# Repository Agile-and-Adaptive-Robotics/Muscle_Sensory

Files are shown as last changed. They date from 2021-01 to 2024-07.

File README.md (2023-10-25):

# Muscle-Sensory
Repository for sharing and storing muscle sensory project related information.
- BallisticShield has solid models for creating ballistic shield to protect experimenters from potential catastrophic BPA failure.
- BPA_End_Caps contains solid models for different types of BPA end caps.
- BPA_Static_Characterization_Test contains files and folders for projects that attempt to characterize the relationship between isometric force, pressure, and contraction. Mostly from Lawrence's incomplete Master's project.
- Leak-Fill_tests contains files from Ben Bolen's mechatronics final project. It is designed to test how quickly a BPA can inflate, and a second test to measure how much pressure a BPA might leak over time.
- Muscle_length_sensory should contain files for real-time muscle length sensory projects. It has files from Jake Chung's Master's project, but doesn't appear to have the files from Connor B.'s Master's project using LiquidWire.
- Muscle_Tension_Sensory contains files for muscle tension sensory projects. Currently it has files from part of Jordan Huddleson's Master's project.
- Pulse testing contains files pertaining to force testing of isometric BPAs using pulsing of BPAs. Current has FrequencyIterationBPATestingCode2 contains an Arduino file that is designed to pulse BPAs in a static jig. It was a project by David P., helped by others (including Cody S.). Will include Mo's testing, too.

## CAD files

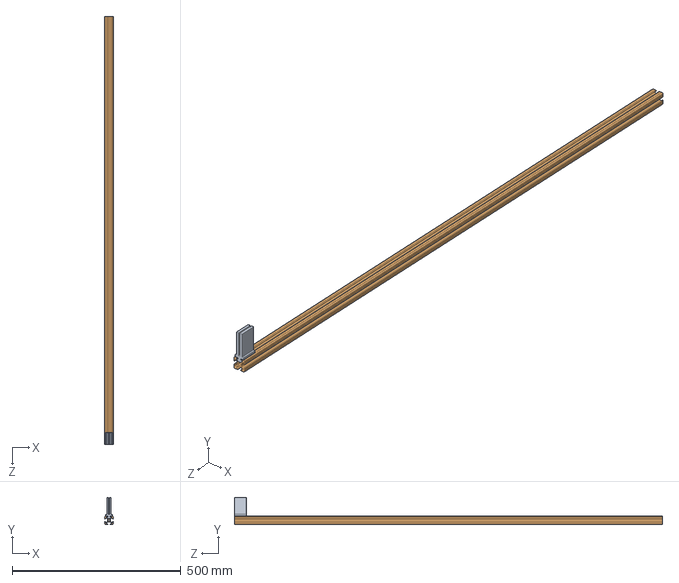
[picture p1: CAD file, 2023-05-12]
BallisticShield/Assem1.SLDASM
25.4 x 80.4 x 1270.0 mm
PolycarbClip
8020-1010 X 50

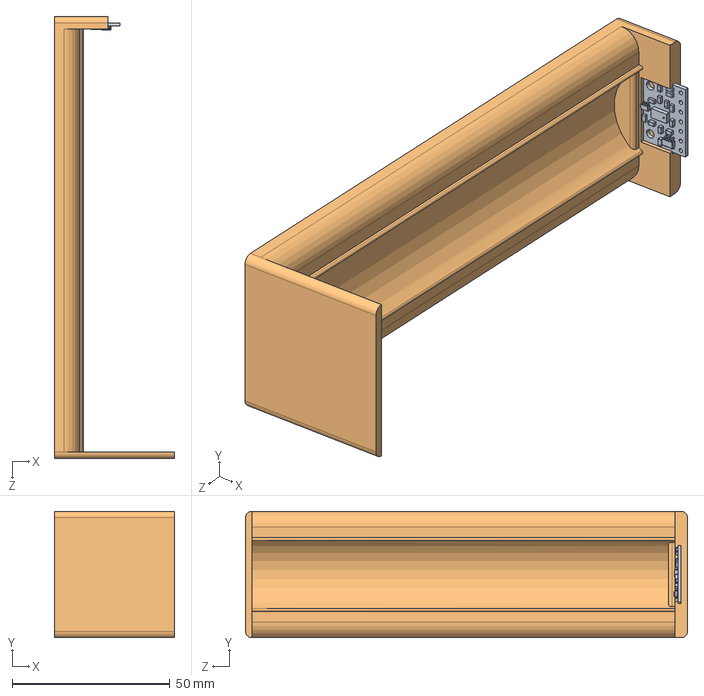
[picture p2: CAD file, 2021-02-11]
Muscle_length_sensory/IR_TOF/circuitTestStand/testStand.SLDASM
38.0 x 40.0 x 140.0 mm
vl53l0x-vl53l1x-vl53l3cx-carrier-model.step
testStand_direct

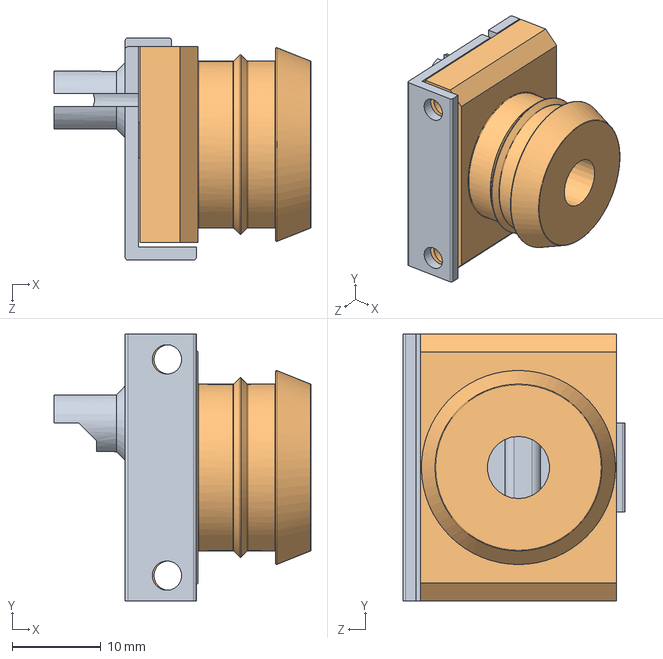
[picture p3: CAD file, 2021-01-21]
Muscle_length_sensory/IR_TOF/sensorEnd.SLDASM
28.9 x 30.0 x 25.0 mm
sensorCap
sensorEnd

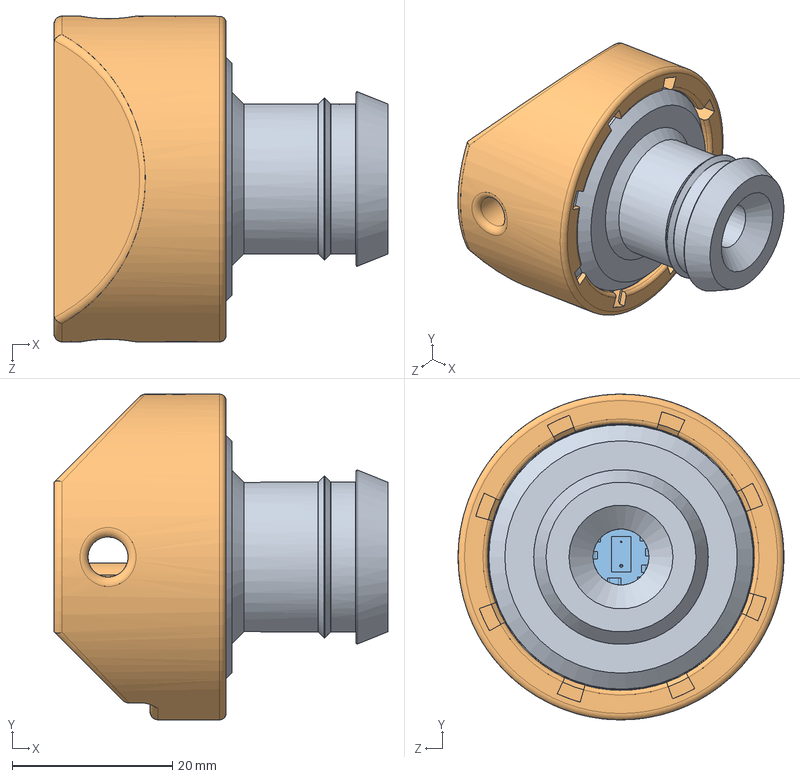
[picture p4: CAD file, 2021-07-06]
Muscle_length_sensory/IR_TOF_circular_housing/circularHousing_withMounting.SLDASM
41.7 x 40.7 x 40.7 mm
sensorEnd_CircularHousing
sensorCap_circularHousingMounting
vl53l0x-vl53l1x-vl53l3cx-carrier-model.step

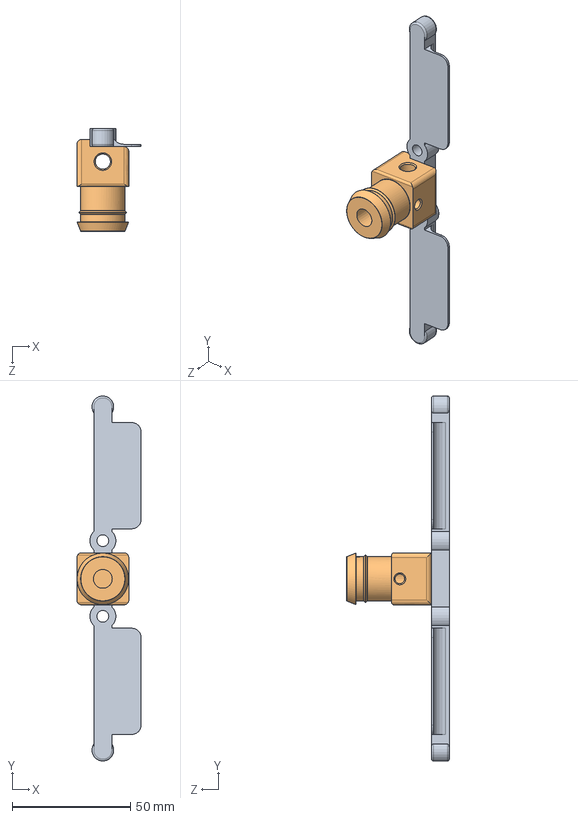
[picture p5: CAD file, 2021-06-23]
Muscle_length_sensory/testFixture/testFixtureAssembly.SLDASM
27.2 x 154.4 x 43.5 mm
80_20_sliding_stabilizer
modified_AARL_Puppy_18_02_01_012_Festo20mm_U10port

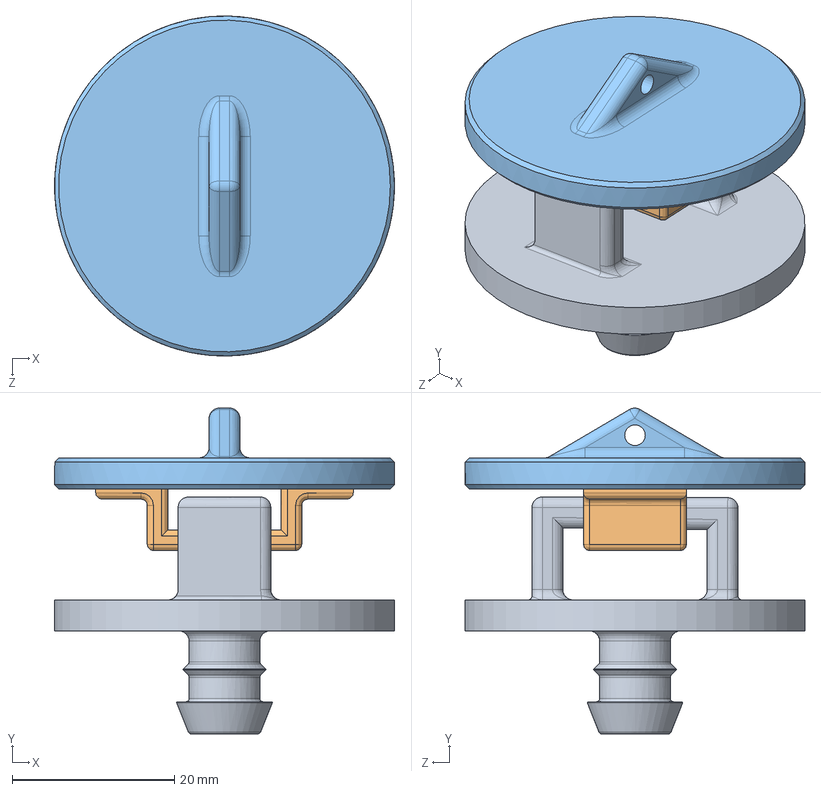
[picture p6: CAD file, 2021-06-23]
Muscle_Tension_Sensory/CAD_Mechanical/AARL_IB-Type_Ib/AARL_IB_002-Compression_Sensor.SLDASM
41.9 x 40.2 x 41.9 mm
AARL_IB_ST_003
AARL_IB_ST_004
AARL_IB_ST_002

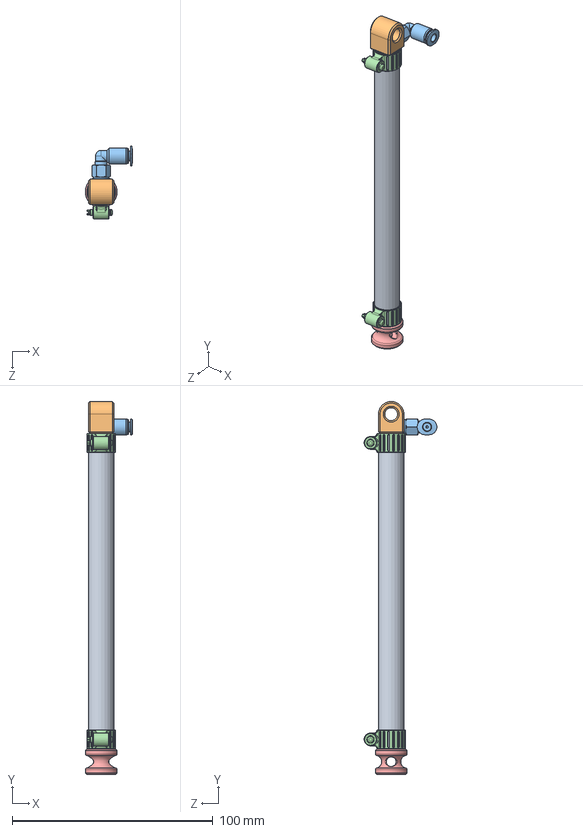
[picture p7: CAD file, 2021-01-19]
BPA_End_Caps/AARL_Puppy_18_02_01_000.SLDASM
23.6 x 185.8 x 36.2 mm
AARL_Puppy_18_02_01_001
AARL_Puppy_18_02_01_002
AARL_Puppy_18_02_01_004-QSML-M3-4
AARL_Puppy_18_02_01_005-SK-8-16 x 2
AARL_Puppy_18_02_01_007

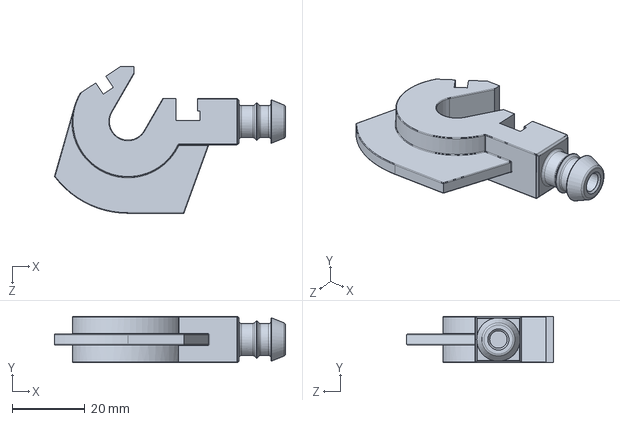
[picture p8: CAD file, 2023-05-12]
BPA_Static_Characterization_Test/Solid_models/BPA10-Hook Assembly.SLDASM
63.3 x 12.7 x 40.2 mm

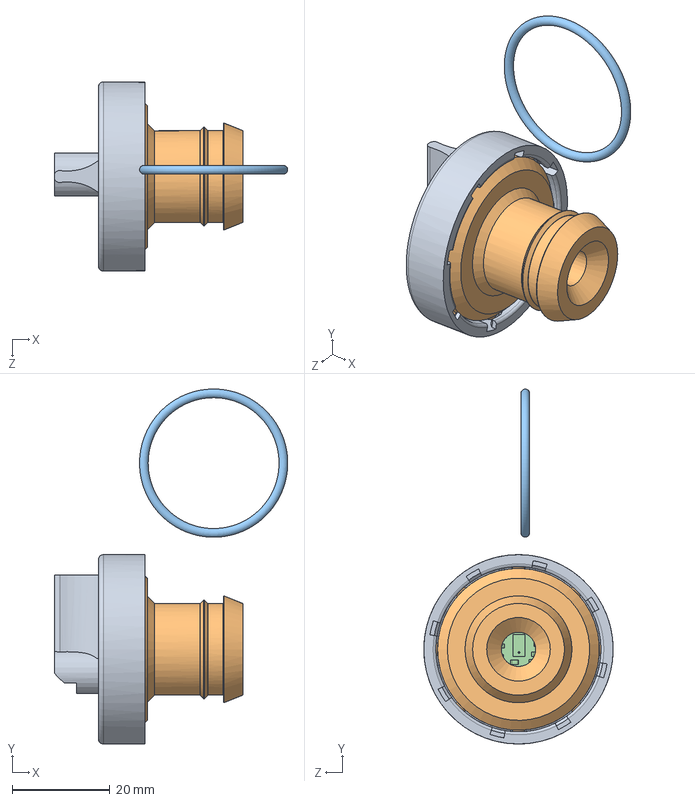
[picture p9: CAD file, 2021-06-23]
Muscle_length_sensory/IR_TOF_circular_housing/circularHousing.SLDASM
47.6 x 72.5 x 38.6 mm
sensorCap_circularHousing
sensorEnd_CircularHousing
vl53l0x-vl53l1x-vl53l3cx-carrier-model (1).step

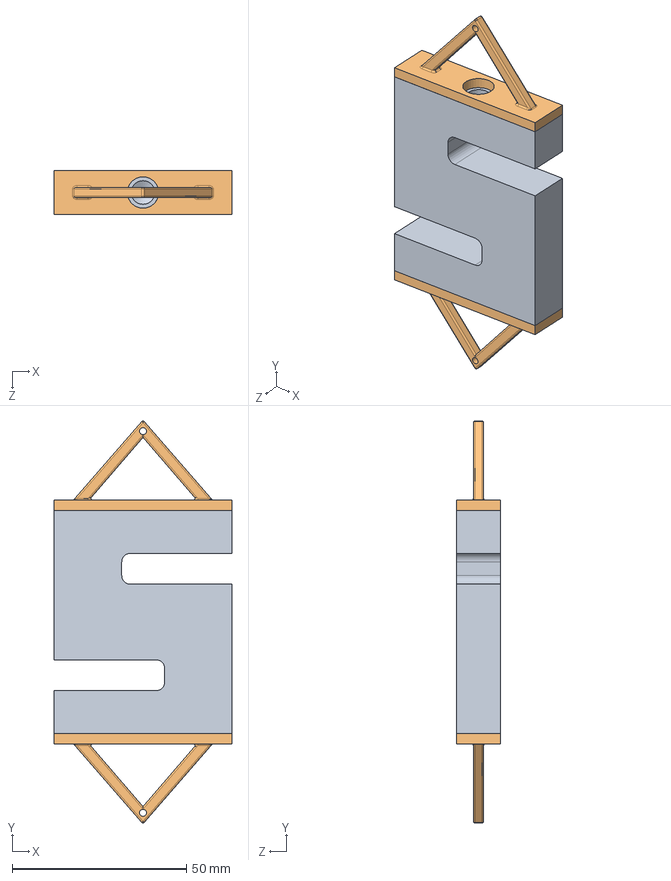
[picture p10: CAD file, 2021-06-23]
Muscle_Tension_Sensory/CAD_Mechanical/AARL_IB-Type_Ib/AARL_IB_001-S_Load_Cell.SLDASM
51.0 x 115.5 x 12.7 mm
AARL_IB_EL_001-S_Load_Cell
AARL_IB_ST_001-S_Plate x 2

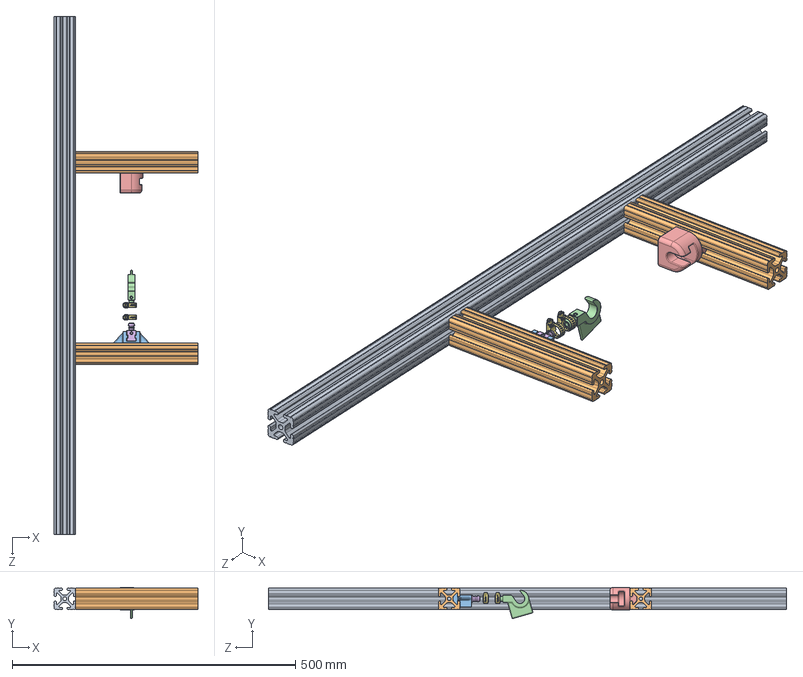
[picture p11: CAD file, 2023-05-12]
BPA_Static_Characterization_Test/Solid_models/Static Test Assembly.SLDASM
254.0 x 54.9 x 914.4 mm
8020-1515 X 36
1515_8_5_CL x 2
BPAConnectionToFrame_10
BPAtoMeter_10
MeterToFrame_002
PlugForFrame_10
AARL_Puppy_18_02_01_009-5388K140_Hose-Clamp x 2

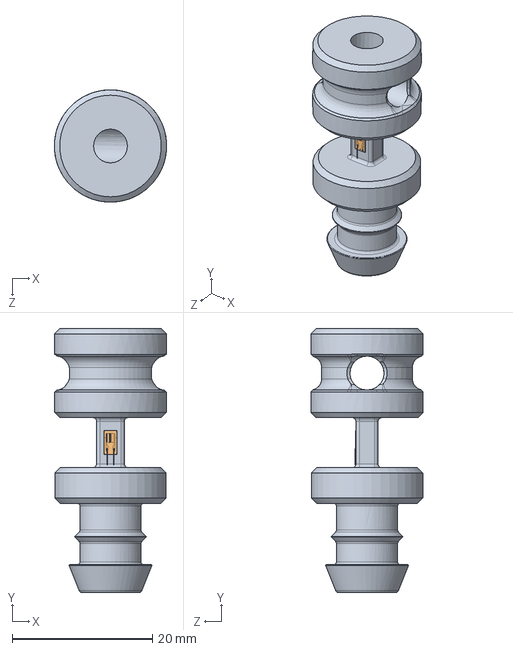
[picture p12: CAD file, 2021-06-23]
Muscle_Tension_Sensory/CAD_Mechanical/AARL_IB-Type_Ib/AARL_IB_003-Strain_Gauge.SLDASM
16.0 x 37.6 x 16.0 mm
AARL_IB_ST_005
AARL_IB_EL_002-Strain_Gauge

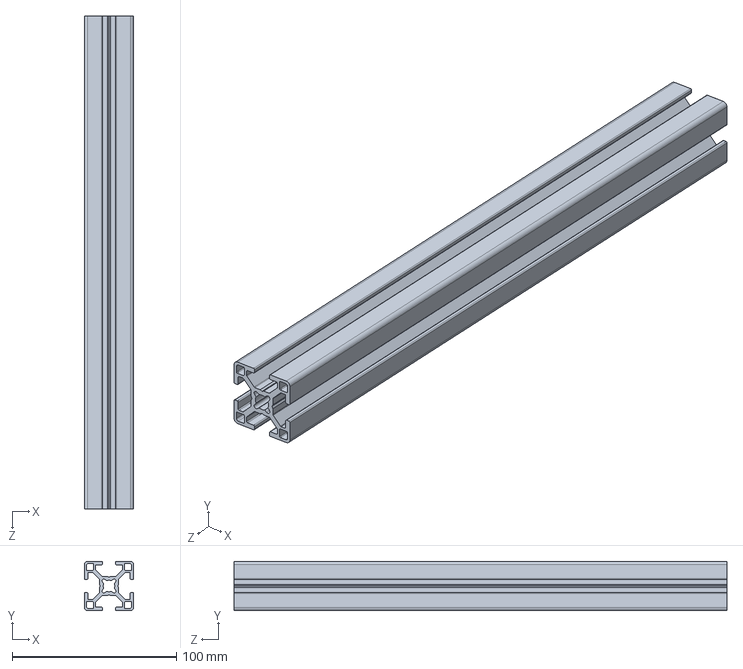
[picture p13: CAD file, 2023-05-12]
BallisticShield/30_Series/30-3030.sldprt
30.0 x 30.0 x 300.0 mm

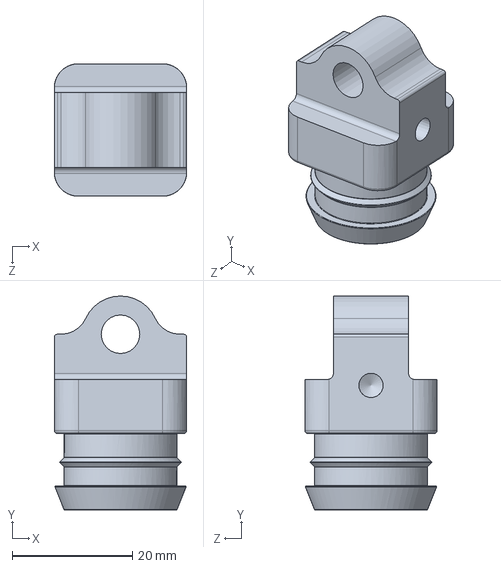
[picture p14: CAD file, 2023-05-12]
BPA_End_Caps/AARL_Puppy_18_02_01_012_Festo20mm_U10port_Law.SLDPRT
22.0 x 35.5 x 22.0 mm

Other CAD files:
BPA_Static_Characterization_Test/Solid_models/Static Test Assembly - 10mm.SLDASM
BPA_Static_Characterization_Test/Solid_models/BPA_Stronger_Mounting_Hooks/fit test.SLDPRT
BPA_Static_Characterization_Test/Solid_models/DesignedParts/Endcap_20mm_Cable.SLDPRT
BPA_Static_Characterization_Test/Solid_models/PlugForFrame_20mm_NoPorts.SLDPRT
BPA_End_Caps/AARL_Puppy_18_02_01_001.SLDPRT
BPA_End_Caps/AARL_Puppy_18_02_01_002.SLDPRT
BPA_End_Caps/AARL_Puppy_18_02_01_002.STL
BPA_End_Caps/AARL_Puppy_18_02_01_003.SLDPRT
BPA_End_Caps/AARL_Puppy_18_02_01_004-QSML-M3-4.sldprt
BPA_End_Caps/AARL_Puppy_18_02_01_005-SK-8-16.SLDPRT
BPA_End_Caps/AARL_Puppy_18_02_01_006.SLDPRT
BPA_End_Caps/AARL_Puppy_18_02_01_007.SLDPRT
BPA_End_Caps/AARL_Puppy_18_02_01_007.STL
BPA_End_Caps/AARL_Puppy_18_02_01_008.SLDPRT
BPA_End_Caps/AARL_Puppy_18_02_01_008.STL
BPA_End_Caps/AARL_Puppy_18_02_01_010.SLDPRT
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

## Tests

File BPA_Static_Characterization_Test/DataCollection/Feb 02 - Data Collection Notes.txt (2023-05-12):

20 mm BPA testing
Already Done: 12 (15) cm, 23 (25.3) cm, 27.5 (30) cm. Need a longer and shorter test.

FEB 02 2022: 

Collect Data for 20mm BPA: 

-----------------------------------------------------------------------------------------------------------
BPA length: 42.7 cm 
 39.7 cm(measured from clamped end to end)

Diameter :20mm

Max contraction length (measured clamp end to end @ 620kPa):  29.6 cm
Contraction: resting length - max contraction length = 39.7 cm - 29.6 cm = 10.1  cm

NOTES:

First attemp to run test, when the BPA was pressurized the bolt connecting the BPA to the load cell pulled out of the threads.
Tried to thread the bolt in further, and was unsuccessful.  Threaded in as far as possible (by hand), and ran test again, appears 
to be holding. Bolt does not appear to be correctly sized, unless the threads on the load cell aren't standard

 -------------------
Kinked: 3.5 cm
-------------------
Kinked: 4.6 cm

NOTE:

Data for last test appears weird. MATLAB command window noted spike, and the pressure spikes off the chart, while the force goes 
off at about 10 o'clock. Saved data, ran the last test again (test 10)

Ran Offset, Test 10, and all data appeared normal. Saved in seperate file, continuing testing.

-------------------
Kinked: 6.9 cm

-----------------------------------------------------------------------------------------------------------
-----------------------------------------------------------------------------------------------------------
BPA length: 12.4 cm 
 9.8 cm(measured from clamped end to end)

Diameter :20mm

Max contraction length (measured clamp end to end @ 620kPa):  7.4 cm
Contraction: resting length - max contraction length = 9.8 cm - 7.4 cm = 2.4 cm

NOTE: 

 -------------------
Kinked: 1.3 cm
-------------------
Kinked: 2.0 cm

-----------------------------------------------------------------------------------------------------------

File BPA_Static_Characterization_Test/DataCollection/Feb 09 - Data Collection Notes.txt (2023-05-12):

Data for Ben

42.7 cm

20 mm BPA testing

FEB 09 2022: 

Collect Data for 20mm BPA: 

-----------------------------------------------------------------------------------------------------------
BPA length: 45.1 cm 
 42.7 cm(measured from clamped end to end)

Diameter :20mm

Max contraction length (measured clamp end to end @ 620kPa):  34.4 cm
Contraction: resting length - max contraction length = 42.7 cm - 34.4 cm = 8.3 cm

NOTES:

20 mm BPA currently installed on knee was measured at 42.7 cm from clamp to clamp, and then a new BPA was cut 
and installed on the test rig.

-------------------
Kinked: 1.0 cm
-------------------
Kinked:  3.0 cm
-------------------
Kinked:  4.0 cm

-----------------------------------------------------------------------------------------------------------
-----------------------------------------------------------------------------------------------------------
BPA length: cm 
 cm(measured from clamped end to end)

Diameter :20mm

Max contraction length (measured clamp end to end @ 620kPa):  cm
Contraction: resting length - max contraction length = cm - cm = cm

NOTE: 

 -------------------
Kinked: cm
-------------------
Kinked:  cm

-----------------------------------------------------------------------------------------------------------

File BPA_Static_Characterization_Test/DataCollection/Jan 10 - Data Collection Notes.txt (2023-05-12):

Jan 10

Comment: Pressure and Load data (check column)

BPA length: 29.8cm 

28.1cm(measured from clamped end to end)

Diameter :10mm
Max contraction length (measured clamp end to end @ 620kPa): 23.6cm
Contraction: resting length - max contraction length = 28.1 - 23.6 = 4.5

-------------------
Kinked:1.7cm
-------------------
Kinked:2.8cm
-------------------
Kinked:4.1cm

#####################################################################################################

BPA length: 27.6 cm 
25.7 cm(measured from clamped end to end)

Diameter :10mm

Max contraction length (measured clamp end to end @ 620kPa): 22.1 cm
Contraction: resting length - max contraction length = 25.7 cm - 22.1 cm = 3.6 cm

 -------------------
Kinked: 0.7 cm
-------------------
Kinked: 1.5 cm
-------------------
Kinked: 3.1 cm

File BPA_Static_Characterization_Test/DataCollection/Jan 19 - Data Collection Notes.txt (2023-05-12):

James's 20mm BPA Adventures

Jan 19 2022: 

Collect Data for 20mm BPA: 

-----------------------------------------------------------------------------------------------------------
BPA length: 25.3 cm 
22.8 cm(measured from clamped end to end)

Diameter :20mm

Max contraction length (measured clamp end to end @ 620kPa):  17.3 cm
Contraction: resting length - max contraction length =  22.8 cm - 17.3 cm = 5.5 cm

NOTE: Data Saved as 23 cm due to not having original (unclamped) length available at start.

 -------------------
Kinked: 0.9 cm
-------------------
Kinked: 1.9 cm

Data Jumped (load cell bolt sliped some) on second to last data set, will repeat the data set to be sure all data is good
-------------------
Kinked: 1.9 cm

Repeated data point

-----------------------------------------------------------------------------------------------------------

BPA length: 15.0 cm 
 12.0 cm(measured from clamped end to end)

Diameter :20mm

Max contraction length (measured clamp end to end @ 620kPa):  9.5 cm
Contraction: resting length - max contraction length =  12.0 cm - 9.5 cm = 2.5 cm

Note: Data Saved as 12 cm due to not having unclamped length available at start. Attemped to resolve the load cell bolt slipage problem by 
inserting a block of nuts and duct tape and using a hose clamp to hold it in place.

 -------------------
Kinked: 1 cm
-------------------
Kinked: 2.0 cm

-------------------
Kinked:  cm

-----------------------------------------------------------------------------------------------------------

BPA length: 30.0 cm 
 27.5 cm(measured from clamped end to end)

Diameter :20mm

Max contraction length (measured clamp end to end @ 620kPa):  20.7 cm
Contraction: resting length - max contraction length = 27.5 cm - 20.7 cm = 6.8 cm

 -------------------
Kinked: 1.4 cm
-------------------
Kinked: 2.3 cm
-------------------
Kinked: 3.4 cm

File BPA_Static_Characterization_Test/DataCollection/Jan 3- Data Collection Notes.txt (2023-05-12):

Jan 3 - Data Collection Notes
---------------------------------
BPA length: 23cm 
21.9cm(measured from clamped end to end)
Diameter :10mm
Max contraction length (measured clamp end to end @ 620kPa): 18.6cm
Contraction: resting length - max contraction length = 21.9 - 18.6 = 3.3

Data Collection set 1: Unkinked
Note: Force is collected using raw arduino output

---------------------------
Kinked:14mm
---------------------------
Kinked: 30mm
comments: Might be too much slack. hence not enough force. 

---------------------------

#######################################################################################################

BPA length: 30cm
28.1cm(measured from clamped end to end)
Diameter :10mm
Max contraction length (620kPa): 24cm
Contraction: resting length - max contraction length = 28.1 -24 = 4.1

Kinked: 1.2cm
----------------------------------
Kinked: 2.2cm
----------------------------------
Kinked: 3.3cm

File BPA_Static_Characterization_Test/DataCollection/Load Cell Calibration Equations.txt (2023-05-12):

10mm 
force (N) = ((Arduino Output*0.1535)-1.963)*4.45

20mm 
force(N) = (Arduino Output*0.392)-4.1786)*4.45

40mm
force(N) = ((ArduinoOutput)*1.395 - 14.661)*4.45

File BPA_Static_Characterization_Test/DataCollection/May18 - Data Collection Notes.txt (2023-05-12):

40mm Data collection:

1) Debugging and checking sensor signals
Data is collected using ValvePWM_mod : no force equation is applied. Reading analogRead for both pressure and force. 
Note: Pressure spikes a lot because of pressure sensor placement

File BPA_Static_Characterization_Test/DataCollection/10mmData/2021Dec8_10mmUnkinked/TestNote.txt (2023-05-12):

BPA length at clamp end: 12cm
Max contraction length:10cm
contraction: 2cm
Pressure Sensor Placement: Outlet of BPA

-------------------------------------------------------------------------------------------------------------------
Inlet Valve Timing: 10ms per 500ms
Outlet Valve Timing: 30ms per 500ms (Note: sub 30ms the valve wouldn't release gas even though it switches) 
	Test 1 and 2 Comments:Pressure settles at about 200kPa when using 30ms for outlet valve :( 

-------------------------------------------------------------------------------------------------------------------
Inlet Valve Timing: 10ms per 500ms
Outlet Valve Timing: 40ms per 500ms

Test 3 : Pressure settles at about 100kPa. 
Test 4: Added tape to cover silencer holes2? Still same shit. 

-------------------------------------------------------------------------------------------------------------------

Inlet Valve Timing: 10ms per 500ms
Outlet Valve Timing: 60ms per 500ms

Test5: 100kPa

Test6: 100kPa 

----------------------------------------------
Inlet Valve Timing: 5ms per 500ms
Outlet Valve Timing: 40ms per 500ms

Test7: 100kpa. 

Test 8: 100kpa.

---------------------------------------------
Inlet Valve Timing: 5ms per 500ms
Outlet Valve Timing: 50ms per 500ms

Test 9: sub 100kpa. 
Test 10:sub 100kpa

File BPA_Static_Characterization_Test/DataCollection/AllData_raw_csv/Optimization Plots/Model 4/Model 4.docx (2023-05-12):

Testing 10mm 13cm vs 20mm40cm parameters:

Model 4: Force = (a0 + a1(e/emax))*pressure + a2(e/emax) + a3;

Force = a3 + a2*(relative strain) + (ao + a1*relativestrain)*Pressure

Regression analysis:

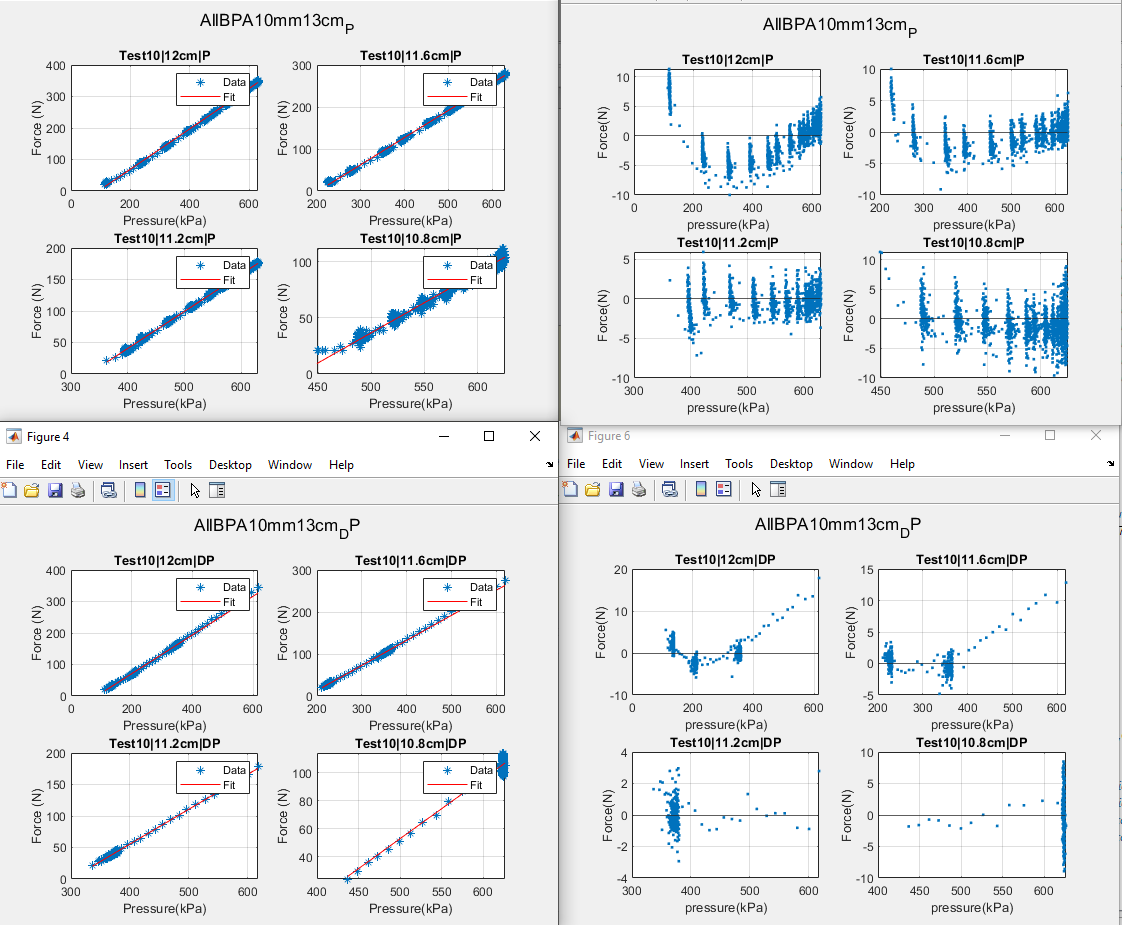
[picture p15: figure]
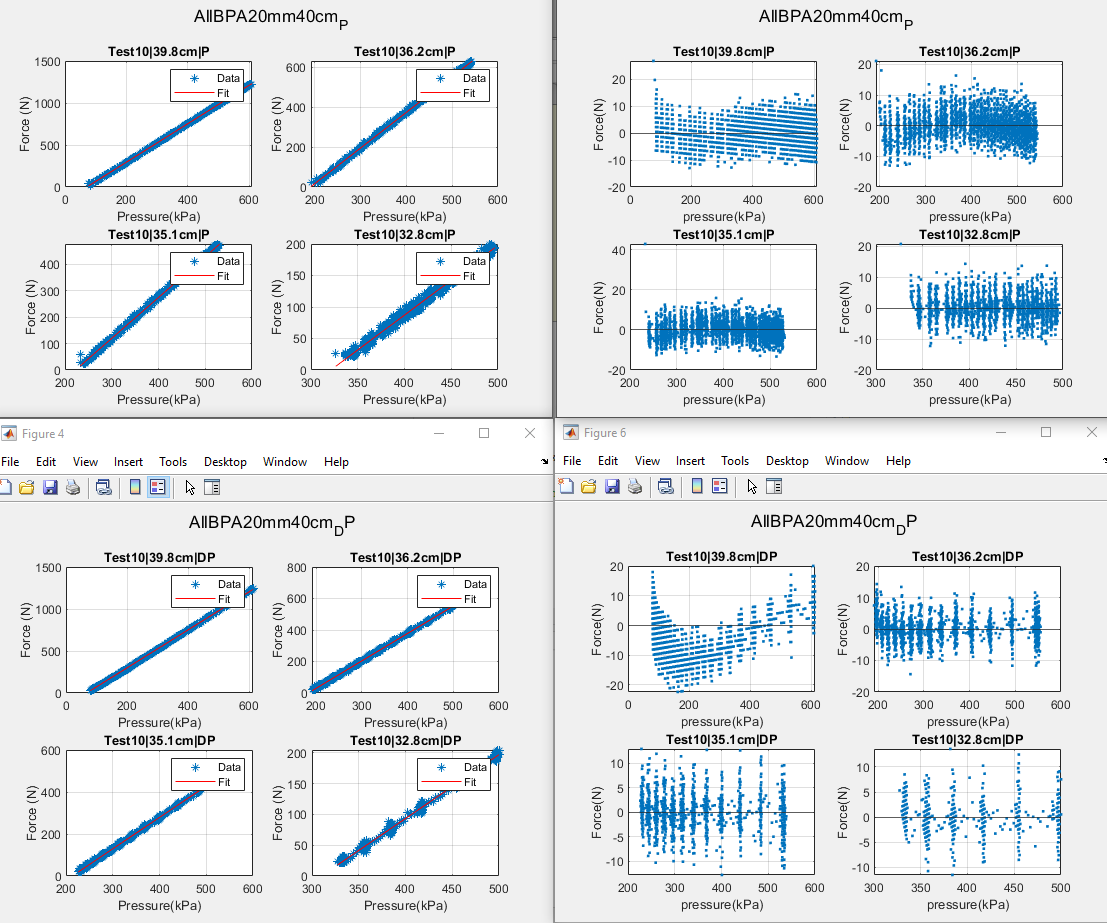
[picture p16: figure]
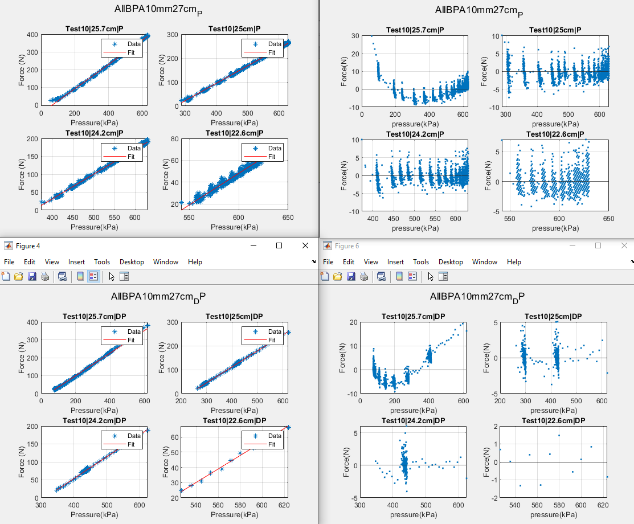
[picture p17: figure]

\

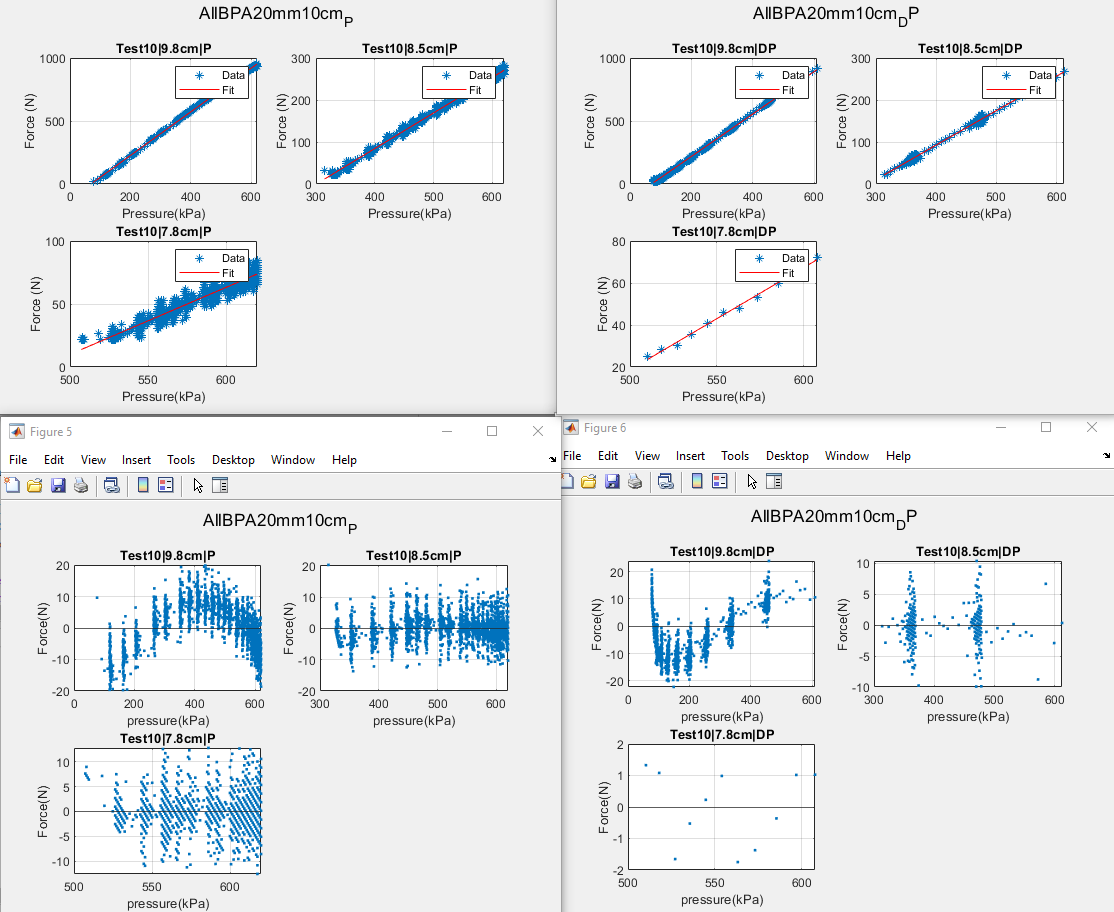
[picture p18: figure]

10mm13cm

10mm27cm

20mm40cm

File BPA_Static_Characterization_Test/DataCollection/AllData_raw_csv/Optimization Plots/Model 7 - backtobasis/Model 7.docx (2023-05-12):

Model Equation: Force = B0 + B1*Pressure

Description: To study how BPA force is related to Pressure, Diameter, Strain, length, and P/DP state, we need to study how B0 and B1 changes with these variables. Check if Force = f(P,D,L,e,S)

Slope (B1):

- 10mm BPA :
  - as length increases (all unkink), the slope increases almost linearly.
  - Depressurizing has lower slope compared to Pressurizing (line shifted downwards)
- 20mm BPA:
  - As length increases (all unkink), the slope increases linearly until 40cm length.
  - Depressurizing has lower slope compared to pressurizing (line shifted downwards, same as 10mm)
- 10mm vs 20mm
  - 20mm has steeper increases in slope (D affects slope!)

Conclusion: D and L affects slope.

    - Increasing D increases slope
    - Increasing L increases slope
    - State affects slope by shifting B1 up or down depending on P or DP. (S)

10mm BPA:

- For the same length: Increasing strain (Eg: kink), decreases slope. Or, shorter Lo decreases slope. (increasing strain decreases slope-nonlinear)
- Depressurizing has lower slope – as stated above.
- Increasing length increases slope.

20mm BPA:

- For the same length, increasing strain decreases slope linearly. (L,e,D,S)
- Increasing length increases slope. (Shift curve upwards).

Conclusion:

    - Increasing D increases slope (D)
    - Increasing L increases slope (L)
    - State affects slope by shifting B1 up or down depending on P or DP. (S)
    - Increasing strain decreases slope (e)

Question: Do I use strain or (1-relative strain)? Also, since BPA resting length and strain affects the slope, would it be better to use Lo*(1-relative strain) to get an “Effective length or working length” of the BPA as a parameter?

Intercept (BO)

For 10mm BPA :

  - Increasing length increases intercept within all unkink
  - DP has higher intercept for all lengths

For 20mm BPA:

- Pretty random (not much correlation in length and Bo)
- DP has higher intercept compared to P.

Conclusion:

    - We cannot say that L and D affect intercept.
    - State (S) affects intercept by shifting curve up or down.
- 10mm:
  - For all unkink, increasing length doesn’t show a pattern in B0 > Maybe I should try L*(relative strain)
  - State: DP has higher B0 compared to P.
  - Increasing strain decreases intercept (B0)
- 20mm
  - For all unkink, increasing length doesn’t show a pattern in B0 > Maybe I should try L*(relative strain)
  - State: DP has higher B0 compared to P.
  - Increasing strain decreases intercept (B0)
- Comparing 10mm and 20mm:
  - Shape of curve are similar for 10mm and 20mm data; however 20mm data has a smaller range of B0 compared to 10mm data.

Conclusion:

- B0 is affected by the state of Pressurizing or depressurizing (S), diameter (D), and strain(e)
- We might need to plot B0 against L0*(1-relativestrain) to see if there’s any pattern.

Trying Lo*(1-relative strain)

- Better results compared to Bo vs relative strain
- 10mm:
  - P/DP: pressurizing has lower intercept (shifted downwards)
  - For the same length: Lo*(1-relative strain) – increasing it increases Bo (increases strain decreases Bo)
  - For all unkink: increasing length decreases Bo. (longer BPA has lower intercept Bo)
- 20mm:
  - Same as 10mm
- Comparing 10mm and 20mm:
  - B0 curve has similar general shape in both 10mm and 20mm; however, 20mm has better separation between different lengths.

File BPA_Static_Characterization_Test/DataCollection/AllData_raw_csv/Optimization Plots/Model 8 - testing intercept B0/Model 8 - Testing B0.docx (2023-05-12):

Model 8: Force = c0 + c1(1-Erel)^2 + c2(P)

Description: Testing if (1-Erel)^2 term is good enough to shift plots to match data.

Note: slope of model shouldn’t be a big concern now since I have not added terms to change the slope.

| C0 | C1 | C2
10mm (P) | -366.9449 | 329.3102 | 0.6785
10mm (DP) | -300.6856 | 284.6008 | 0.5872
20mm (P) | -721.1431 | 748.7470 | 1.7610
20mm (DP) | -676.4303 | 574.5064 | 1.9615

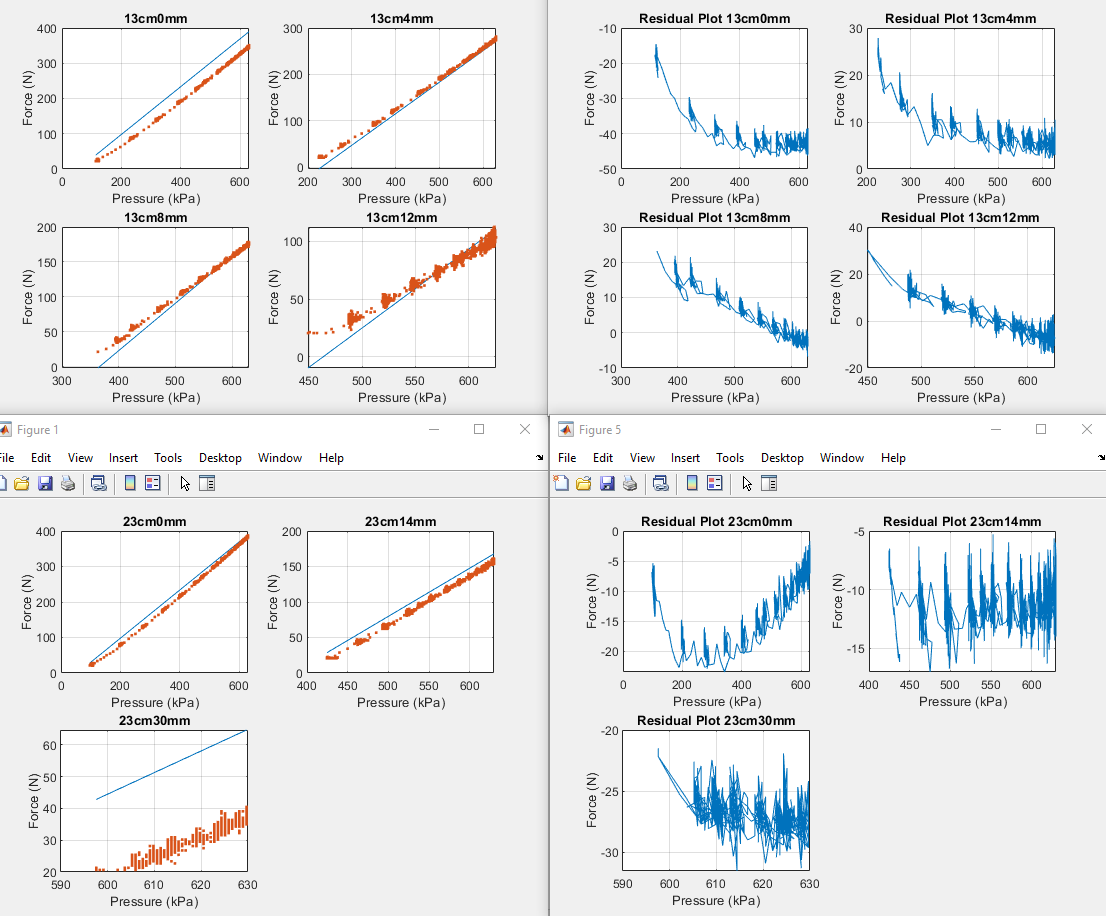
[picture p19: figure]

10mm(Pressurizing)

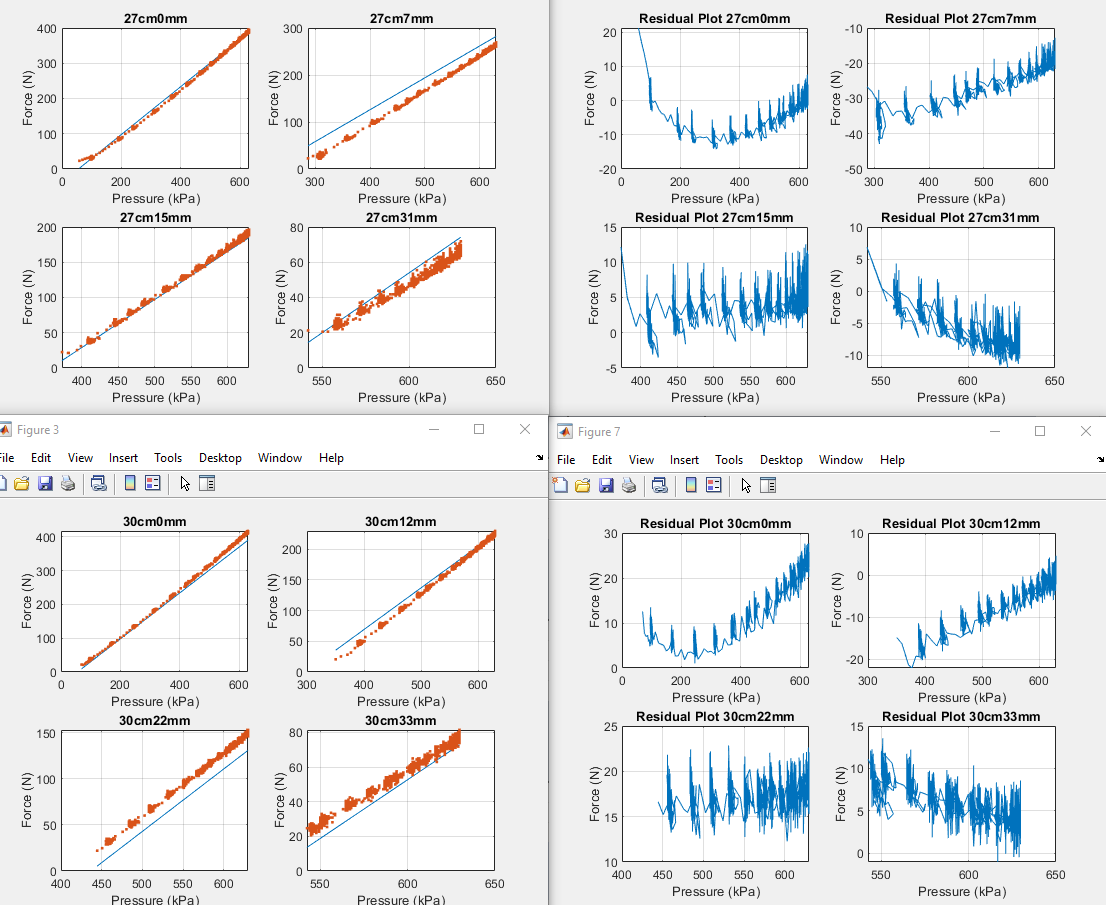
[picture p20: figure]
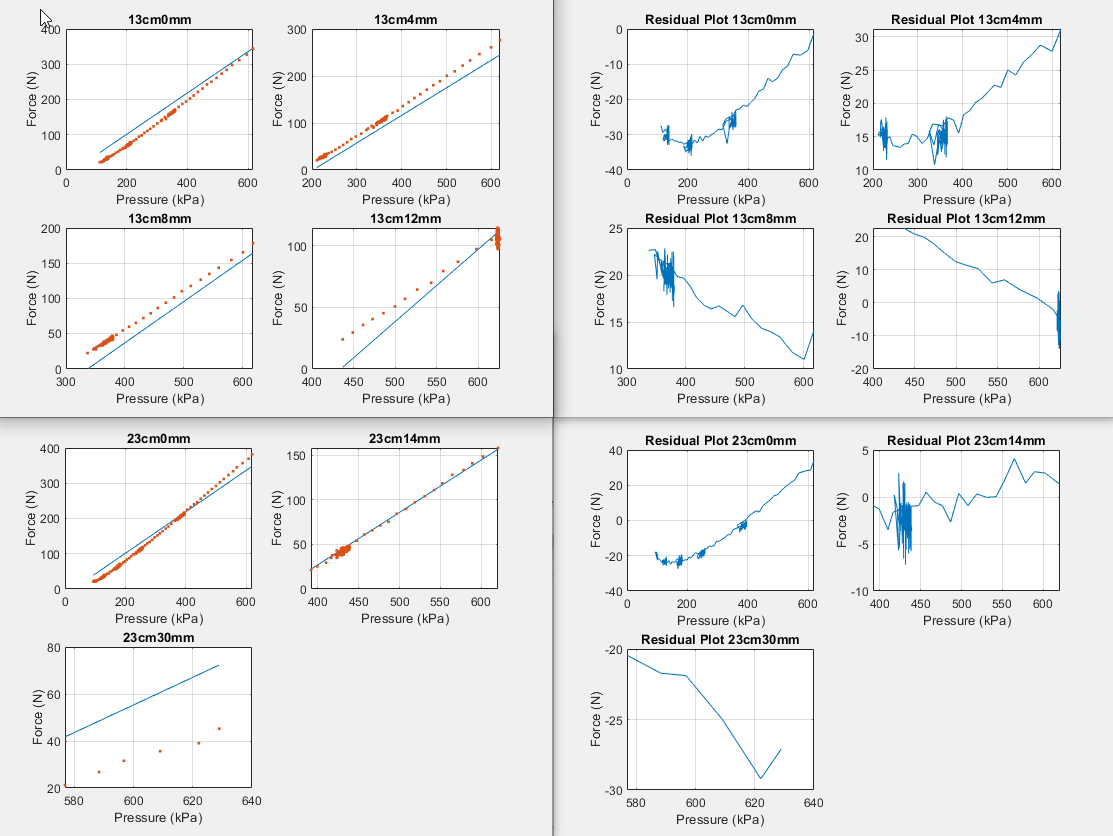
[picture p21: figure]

10mm (Depressurizing)

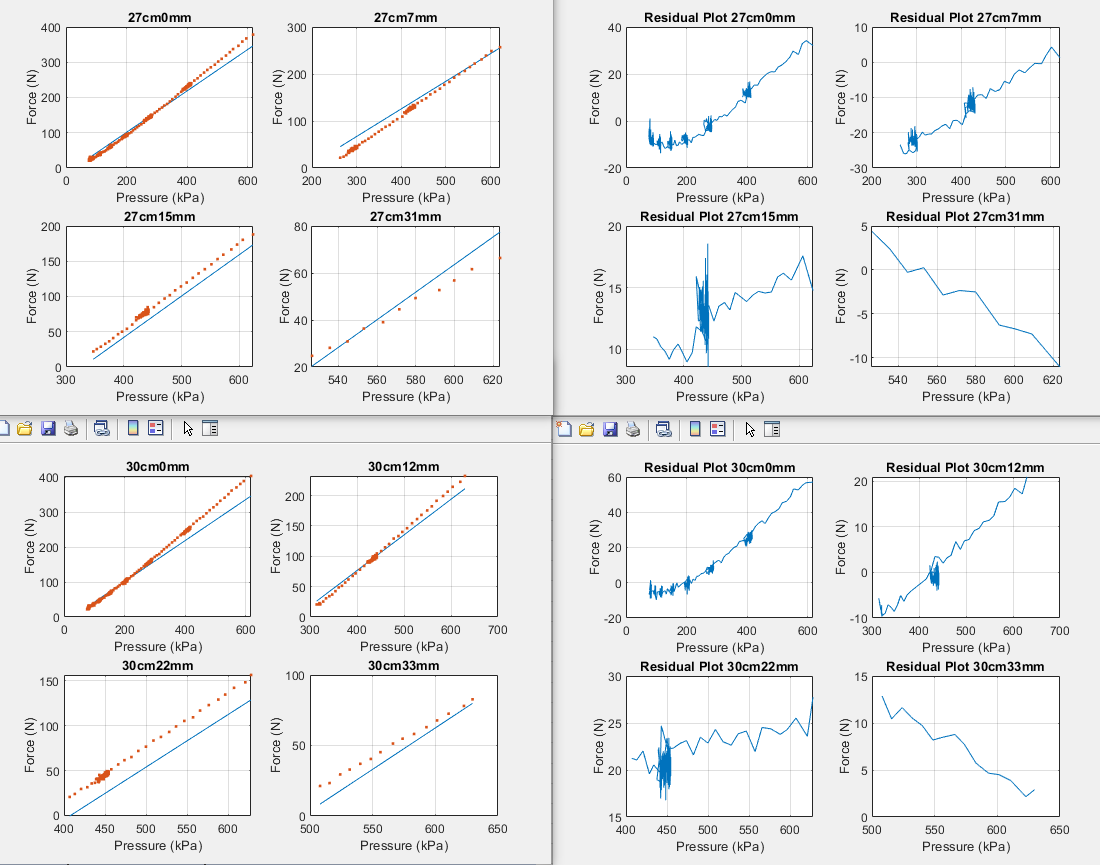
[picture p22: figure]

20mm (Pressurizing)

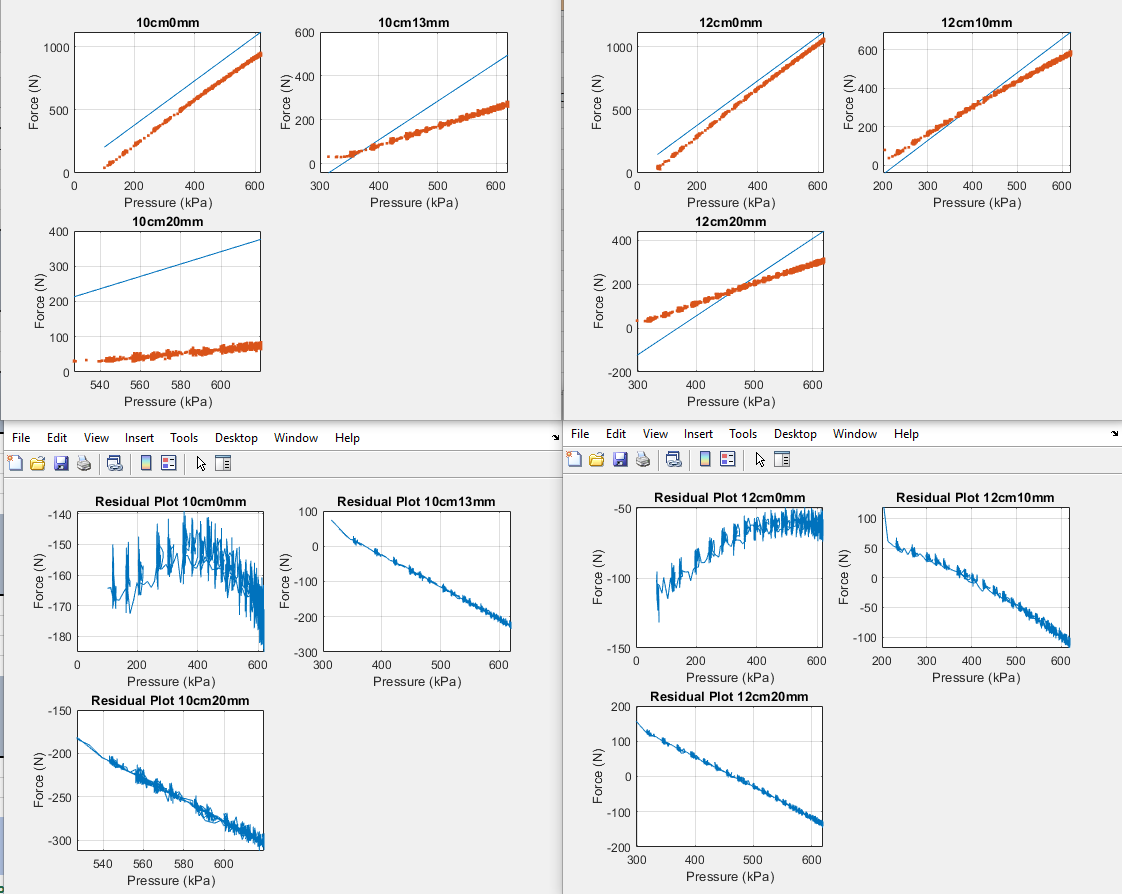
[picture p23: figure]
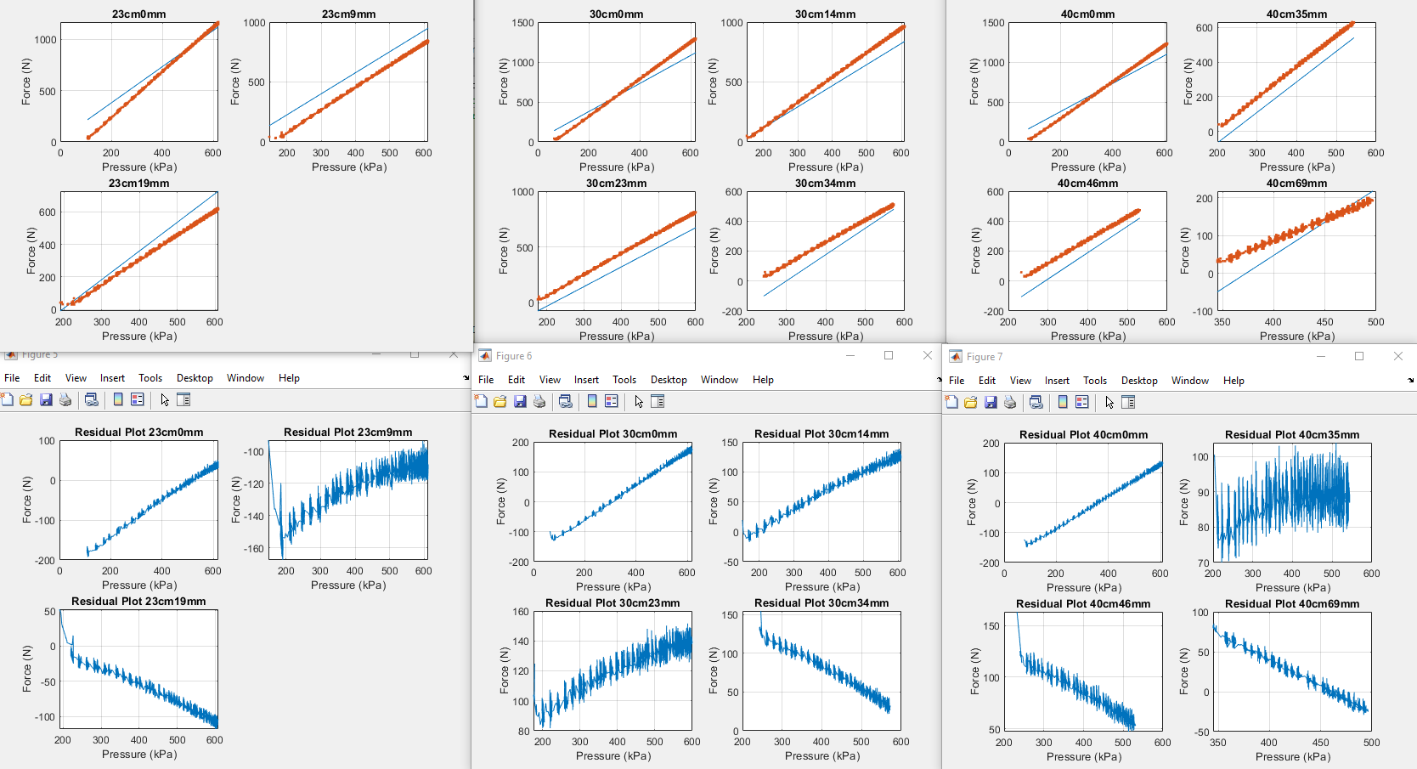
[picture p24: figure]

20mm (Depressurizing)


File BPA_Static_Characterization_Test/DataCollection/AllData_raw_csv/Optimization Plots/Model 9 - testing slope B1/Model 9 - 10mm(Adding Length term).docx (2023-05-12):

B1 – 10mm Model Comparisons


Model: Force = c0 + c1(exp(1-erel))*Pressure +c2(Li)Pressure Force = c0 + c1 (1-Erel)*Pressure+c2(Li)Pressure


Force = c0 + c1(exp(-Erel))Pressure +c2(li)pressure Force = c0 + c1(exp(-Erel^2))Pressure+c2(li)pressure


Force = c0 + c1(1-Erel)^2Pressure + c2(li)Pressure


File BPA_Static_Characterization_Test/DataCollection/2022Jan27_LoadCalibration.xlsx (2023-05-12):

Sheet: 10mm
Load Cell Calibration Data
Note: With 10v excitation, and gain of 100. The range of load cell voltage output is calculated to be [0-3V] for [0-1000lbs]
Jan 5 2022
Load Cell | [0-1000lbs]
Load Cell Voltage Output = (10V)*(3mV/V)*(Gain)*(load/1000lbs)
Gain = 1046 | Resistor 47 Ohm
Weight(lbs) | Weights(N) | Arduino Output(Min) | Arduino Output(Max) | Arduino Output (Averaged) | Experimental Voltage (Calculated) | Experimental Voltage (Measured with scope) | Theoretical Voltage
0 | 0 | 17 | 19 | 18.0 |  |  | 0
5 | 22.25 | 42 | 44 | 43.0 |  |  | 0.015
10 | 44.5 | 74 | 76 | 75.0 |  |  | 0.03
15 | 66.75 | 109 | 112 | 110.5 |  |  | 0.045
20 | 89 | 141 | 144 | 142.5 |  |  | 0.06
25 | 111.25 | 173 | 175 | 174.0 |  |  | 0.075
30 | 133.5 | 207 | 209 | 208.0 |  |  | 0.09
35 | 155.75 | 241 | 243 | 242.0 |  |  | 0.105
37.5 | 166.875 | 258 | 260 | 259.0 |  |  | 0.1125
40 | 178 | 272 | 274 | 273.0 |  | 1.35 | 1.2552
 |  |  |  | 0.0 |  |  | 0
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

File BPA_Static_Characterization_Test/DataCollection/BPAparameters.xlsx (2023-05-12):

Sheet: 10mm
Cut Length (lc) | Resting Length(lo) | Max Contraction Length (lmax) | Initial Kink Length (li) |  |  |  | Cut Length (lc) | Resting Length(lo) | Max Contraction Length (lmax) | Initial Kink Length (li)
13.5 | 12 | 10 | 12 | 10mm13cm all kinks | 1.5 |  | 13.5 | 12 | 10 | 12 | 10mm13cm all kinks
 |  |  | 11.6 |  | 0 |  |  |  |  | 11.6
 |  |  | 11.2 |  | 0 | 0 |  |  |  | 11.2
 |  |  | 10.8 |  | 0 |  |  |  |  | 10.8
23 | 21.9 | 18.6 | 21.9 | 10mm23cm all kinks | 1.1 |  | 23.6 | 21.9 | 18.6 | 21.9 | 10mm23cm all kinks
 |  |  | 20.5 |  | 0 |  |  |  |  | 20.5
 |  |  | 18.9 |  | 0 |  |  |  |  | 18.9
27.6 | 25.7 | 22.1 | 25.7 | 10mm27cm all kinks | 1.9 |  | 27.6 | 25.7 | 22.1 | 25.7 | 10mm27cm all kinks
 |  |  | 25 |  | 0 |  |  |  |  | 25
 |  |  | 24.2 |  | 0 |  |  |  |  | 24.2
 |  |  | 22.6 |  | 0 |  |  |  |  | 22.6
29.8 | 28.1 | 23.6 | 28.1 | 10mm29cm all kinks | 1.7 |  | 29.8 | 28.1 | 23.6 | 28.1 | 10mm29cm all kinks
 |  |  | 26.4 |  | 0 |  |  |  |  | 26.4
 |  |  | 25.3 |  | 0 |  |  |  |  | 25.3
 |  |  | 24 |  | 0 |  |  |  |  | 24
30 | 28.1 | 24 | 28.1 | 10mm30cm all kinks | 1.9 |  | 30 | 28.1 | 24 | 28.1 | 10mm30cm all kinks
 |  |  | 26.9 |  | 0 |  |  |  |  | 26.9
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

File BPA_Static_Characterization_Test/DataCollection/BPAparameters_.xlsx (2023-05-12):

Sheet: 10mm
Cut Length (lc) | Resting Length(lo) | Max Contraction Length (lmax) | Initial Kink Length (li) |  |  |  | Cut Length (lc) | Resting Length(lo) | Max Contraction Length (lmax) | Initial Kink Length (li)
13.5 | 12 | 10 | 12 | 10mm13cm all kinks | 1.5 |  | 13.5 | 12 | 10 | 12 | 10mm13cm all kinks
 |  |  | 11.6 |  | 0 |  |  |  |  | 11.6
 |  |  | 11.2 |  | 0 | 0 |  |  |  | 11.2
 |  |  | 10.8 |  | 0 |  |  |  |  | 10.8
23 | 21.9 | 18.6 | 21.9 | 10mm23cm all kinks | 1.1 |  | 23.6 | 21.9 | 18.6 | 21.9 | 10mm23cm all kinks
 |  |  | 20.5 |  | 0 |  |  |  |  | 20.5
 |  |  | 18.9 |  | 0 |  |  |  |  | 18.9
27.6 | 25.7 | 22.1 | 25.7 | 10mm27cm all kinks | 1.9 |  | 27.6 | 25.7 | 22.1 | 25.7 | 10mm27cm all kinks
 |  |  | 25 |  | 0 |  |  |  |  | 25
 |  |  | 24.2 |  | 0 |  |  |  |  | 24.2
 |  |  | 22.6 |  | 0 |  |  |  |  | 22.6
29.8 | 28.1 | 23.6 | 28.1 | 10mm29cm all kinks | 1.7 |  | 29.8 | 28.1 | 23.6 | 28.1 | 10mm29cm all kinks
 |  |  | 26.4 |  | 0 |  |  |  |  | 26.4
 |  |  | 25.3 |  | 0 |  |  |  |  | 25.3
 |  |  | 24 |  | 0 |  |  |  |  | 24
30 | 28.1 | 24 | 28.1 | 10mm30cm all kinks | 1.9 |  | 30 | 28.1 | 24 | 28.1 | 10mm30cm all kinks
 |  |  | 26.9 |  | 0 |  |  |  |  | 26.9
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

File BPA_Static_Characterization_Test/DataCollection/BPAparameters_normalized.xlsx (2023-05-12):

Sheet: 10mm
BPA ID (10mm) | Cut length | Resting length (lo) | Minimum contraction length (l620) | Initial kink length (li) | Initial contraction | Normalized Initial length | maximum strain | Max strain (%) | strain | Strain (%) | Relative strain
13cm | 13.7 | 12 | 10 | 12 | 0 | 1 | 0.1666666667 | 16.66666667 | 0 | 0 | 0
 | 13.7 | 12 | 10 | 11.6 | 0.4 | 0.9666666667 | 0.1666666667 | 16.66666667 | 0.03333333333 | 3.333333333 | 0.2
 | 13.7 | 12 | 10 | 11.2 | 0.8 | 0.9333333333 | 0.1666666667 | 16.66666667 | 0.06666666667 | 6.666666667 | 0.4
 | 13.7 | 12 | 10 | 10.8 | 1.2 | 0.9 | 0.1666666667 | 16.66666667 | 0.1 | 10 | 0.6
23cm | 23.7 | 22 | 18.5 | 22 | 0 | 1 | 0.1590909091 | 15.90909091 | 0 | 0 | 0
 | 23.7 | 22 | 18.5 | 20.5 | 1.5 | 0.9318181818 | 0.1590909091 | 15.90909091 | 0.06818181818 | 6.818181818 | 0.4285714286
 | 23.7 | 22 | 18.5 | 18.9 | 3.1 | 0.8590909091 | 0.1590909091 | 15.90909091 | 0.1409090909 | 14.09090909 | 0.8857142857
27cm | 27.7 | 25.7 | 21.8 | 25.7 | 0 | 1 | 0.1517509728 | 15.17509728 | 0 | 0 | 0
 | 27.7 | 25.7 | 21.8 | 25 | 0.7 | 0.9727626459 | 0.1517509728 | 15.17509728 | 0.02723735409 | 2.723735409 | 0.1794871795
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

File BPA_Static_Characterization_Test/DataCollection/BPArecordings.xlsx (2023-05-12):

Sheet: Sheet1
BPA Diameter | BPA lengths | BPA kinks |  |  |  | Cut length | Clamped End to End length | Max contration length | Contraction wrt to clamped end | Contraction wrt Cut length
10mm | 13cm | Unkink | 4mm | 8mm | 12mm | 13.5 | 12 | 10 | 2 | 3.5
 | 23cm | Unkink | 14mm | 30mm |  | 23 | 21.9 | 18.6 | 3.3 | 4.4
 | 27cm | Unkink | 7mm | 15mm | 31mm | 27.6 | 25.7 | 22.1 | 3.6 | 5.5
 | 29cm | Unkink | 17mm | 28mm | 41mm | 29.8 | 28.1 | 23.6 | 4.5 | 6.2
 | 30cm | Unkink | 12mm | 22mm | 33mm | 30 | 28.1 | 24 | 4.1 | 6
20mm | 10cm | Unkink | 13mm | 20mm |  | 12.4 | 9.8 | 7.4 | 2.4 | 5
 | 12cm | Unkink | 10mm | 20mm |  | 15 | 12 | 9.5 | 2.5 | 5.5
 | 23cm | Unkink | 9mm | 19mm |  | 25.3 | 22.8 | 17.3 | 5.5 | 8
 | 30cm | Unkink | 14mm | 23mm | 34mm | 30 | 27.5 | 20.7 | 6.8 | 9.3
 | 40cm | Unkink | 35mm | 46mm | 69mm | 42.7 | 39.7 | 29.6 | 10.1 | 13.1
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

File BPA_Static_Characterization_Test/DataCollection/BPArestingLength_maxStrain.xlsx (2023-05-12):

Biomimetic knee
Muscle size | 40
Test | Extensor
Muscle length | 557
Max contracted length | 395
Strain | 0.2908438061
Muscle size | 20
Test | Flexor
Muscle length | 423
Max contracted length | 322
Strain | 0.2387706856
Muscle size | 10
Test | Extensor | Flexor
Muscle length | 520 | 415
Max contracted length | 440 | 350
Strain | 0.1538461538 | 0.156626506
Pinned knee
Muscle size | 10
Test | Extensor |  |  |  | Flexor
Muscle length | 457 | 480 | 486 | 415 | 485 | 455
Max contracted length | 380 | 398 | 405 | 350 | 398 | 378
Strain | 0.1684901532 | 0.1708333333 | 0.1666666667 | 0.156626506 | 0.1793814433 | 0.1692307692
Order by resting length, ascending
10mm ø
Resting Length | 415 | 455 | 457 | 480 | 485 | 486 | 520
Max. Contract | 350 | 378 | 380 | 398 | 398 | 405 | 440
Strain | 0.156626506 | 0.1692307692 | 0.1684901532 | 0.1708333333 | 0.1793814433 | 0.1666666667 | 0.1538461538
20mm ø
Resting Length | 423 |  |  |  |  |  |  | Graph 10mm strain
Max. Contract | 322
Strain | 0.2387706856
40mm ø
Resting Length | 557
Max. Contract | 395
Strain | 0.2908438061
10mm ø (Dr. Hunt)
Resting Length | 153.1 | 182.8 | 189.4 | 195 | 272.7 | 280.9
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

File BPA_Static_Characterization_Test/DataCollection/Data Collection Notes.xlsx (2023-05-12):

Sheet: Dec8 - 10mm13cm
10mm BPA Data Collection
BPA Specification : |  | Resting Length = 12cm |  | Maximum contraction length = 10cm(2cm contraction)
Data | Test # | Inlet Valve Timing | Inlet period | Outlet Valve Timing | Outlet period | Comment
 | 1 | 10 | 500 | 30 | 500
 | 2 | 10 | 500 | 30 | 500
 | 3 | 10 | 500 | 40 | 500
 | 4 | 10 | 500 | 40 | 500
 | 5 | 10 | 500 | 60 | 500
 | 6 | 10 | 500 | 60 | 500
 | 7 | 5 | 500 | 40 | 500
 | 8 | 5 | 500 | 40 | 500
 | 9 | 5 | 500 | 50 | 500 | Best
 | 10 | 5 | 500 | 50 | 500 | Best
Dec 16 - 10mm Kinked
10mm BPA Data Collection
BPA Specification : |  | Resting length = 12cm | Max contraction length = 10cm(2cm) |  | Kinked Length = 1cm | End to end length = 1.2-1.5cm
Data | Test # | Inlet Valve Timing | Inlet period | Outlet Valve Timing | Outlet period | Comment
 | 1 | 10 | 500 | 30 | 500 | Garbage- Pressure doesn’t drop to atm
 | 2 | 10 | 500 | 30 | 500 | Pressure at 200kpa
 | 3 | 10 | 500 | 40 | 500
 | 4 | 10 | 500 | 40 | 500
 | 5 | 10 | 500 | 60 | 500
 | 6 | 10 | 500 | 60 | 500
 | 7 | 5 | 500 | 40 | 500
 | 8 | 5 | 500 | 40 | 500
 | 9 | 5 | 500 | 50 | 500
 | 10 | 5 | 500 | 50 | 500
10mm BPA Data Collection
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

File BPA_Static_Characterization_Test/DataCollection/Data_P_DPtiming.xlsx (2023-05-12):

 |  | Test 1 | Test 2 | Test 3 | Test 4 | Test 5 | Test 6 | Test 7 | Test 8 | Test 9 | Test 10
10mm | 13cm all kinks | 17s
 | 23cm all kinks | 17s
 | 27cm all kinks | 17s
 | 29cm all kinks | 17s
 | 30cm all kinks | 17s
20mm | 10cm all kinks | 20s
 | 12cm all kinks | 23s
 | 23cm all kinks | 25s |  |  | Note: diff test have very different dynamics. Some does not have a steady P v t, hence cannot pinpoint the P/DP area.
 | 30cm all kinks | 25s
 | 40cm all kinks | 29s

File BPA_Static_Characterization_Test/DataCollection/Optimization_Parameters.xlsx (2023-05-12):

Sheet: Sheet1
BPA Diameter | BPA lengths | BPA kinks |  |  |  | Cut length | Clamped End to End length | Max contration length | Contraction wrt to clamped end | Contraction wrt Cut length
10mm | 13cm | Unkink | 4mm | 8mm | 12mm | 13.5 | 12 | 10 | 2 | 3.5
 | 23cm | Unkink | 14mm | 30mm |  | 23 | 21.9 | 18.6 | 3.3 | 4.4
 | 27cm | Unkink | 7mm | 15mm | 31mm | 27.6 | 25.7 | 22.1 | 3.6 | 5.5
 | 29cm | Unkink | 17mm | 28mm | 41mm | 29.8 | 28.1 | 23.6 | 4.5 | 6.2
 | 30cm | Unkink | 12mm | 22mm | 33mm | 30 | 28.1 | 24 | 4.1 | 6
20mm | 10cm | Unkink | 13mm | 20mm |  | 12.4 | 9.8 | 7.4 | 2.4 | 5
 | 12cm | Unkink | 10mm | 20mm |  | 15 | 12 | 9.5 | 2.5 | 5.5
 | 23cm | Unkink | 9mm | 19mm |  | 25.3 | 22.8 | 17.3 | 5.5 | 8
 | 30cm | Unkink | 14mm | 23mm | 34mm | 30 | 27.5 | 20.7 | 6.8 | 9.3
 | 40cm | Unkink | 35mm | 46mm | 69mm | 42.7 | 39.7 | 29.6 | 10.1 | 13.1

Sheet: Optimiaztion Parameters
Best Fit (y=mx+c) | m | c | Force = m*pressure + c
10mm13cmUnkink | 0.647 | -58.6423
10mm13cm4mm | 0.6407 | -125.3122
10mm13cm8mm | 0.5869 | -191.4593
10mm13cm12mm | 0.5451 | -236.8689
10mm23cmUnkink | 0.6921 | -54.6111
10mm23cm14mm | 0.6696 | -261.4865
10mm23cm30mm | 0.6969 | -399.2253
10mm27cmUnkink | 0.6709 | -32.1266
10mm27cm7mm | 0.7167 | -186.1167
10mm27cm15mm | 0.688 | -240.664
10mm27cm31mm | 0.6347 | -332.3549
10mm29cmUnkink | 0.6995 | -14.5988
10mm29cm17mm | 0.7061 | -218.5014
10mm29cm28mm | 0.61 | -265.4358
10mm29cm41mm | 0.6336 | -361.0643
10mm30cmUnkink | 0.7065 | -31.0576
10mm30cm12mm | 0.7282 | -230.8516
10mm30cm22mm | 0.6841 | -280.0296 |  | try poreto search
10mm30cm33mm | 0.6341 | -321.2255
20mm10cmUnkink | 1.7096 | -116.4791
20mm10cm13mm | 0.831 | -245.3959
20mm10cm20mm | 0.5375 | -258.0602
20mm12cmUnkink | 1.836 | -80.2983
20mm12cm10mm | 1.3015 | -222.6048
20mm12cm20mm | 0.8788 | -236.7136
20mm23cmUnkink | 2.1596 | -180.6898
20mm23cm9mm | 1.8066 | -263.6923
20mm23cm19mm | 1.4793 | -283.1843
20mm30cmUnkink | 2.3032 | -134.0187
20mm30cm14mm | 2.0379 | -275.3826
20mm30cm23mm | 1.8558 | -297.8924
20mm30cm34mm | 1.4479 | -317.8912
20mm40cmUnkink | 2.2776 | -155.8118
20mm40cm35mm | 1.7619 | -328.8698
20mm40cm46mm | 1.5215 | -332.5396
20mm40cm69mm | 1.0817 | -343.4428

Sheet: OptimizationParameters EQ2
Model = (a0 +a1*(li-lo)/lo)*Pressure + a2*(li-lo)/lo +a3 |  | Parameters(Pressurizing) |  |  |  |  |  | Parameters(Depressurizing)
Best Fit | mux | a0 | a1 | a2 | a3 | SSE | MUX | a0 | a1 | a2 | a3 | SSE | Comment | Need to redo red highlighted part (wrong li and lo were used)
10mm13cmUnkink |  |  |  |  |  |  |  | {[ 0.6187 -119.0889 5.6971 -40.2975]}
10mm13cm4mm |  |  |  |  |  |  |  | {[87.8422 2.6166e+03 124.6828 -108.6391]}
10mm13cm8mm |  |  |  |  |  |  |  | {[ 36.0653 532.8312 95.4642 -155.7685]}
10mm13cm12mm |  |  |  |  |  |  |  | {[ 14.3226 139.6986 62.3122 -107.7226]}
10mm23cmUnkink
10mm23cm14mm
10mm23cm30mm
10mm27cmUnkink
10mm27cm7mm
10mm27cm15mm
10mm27cm31mm
10mm29cmUnkink
10mm29cm17mm
10mm29cm28mm
10mm29cm41mm
10mm30cmUnkink
10mm30cm12mm
10mm30cm22mm
10mm30cm33mm
20mm10cmUnkink
20mm10cm13mm
20mm10cm20mm
20mm12cmUnkink
20mm12cm10mm
20mm12cm20mm
20mm23cmUnkink
20mm23cm9mm
20mm23cm19mm
20mm30cmUnkink
20mm30cm14mm
20mm30cm23mm
20mm30cm34mm
20mm40cmUnkink
20mm40cm35mm
20mm40cm46mm
20mm40cm69mm

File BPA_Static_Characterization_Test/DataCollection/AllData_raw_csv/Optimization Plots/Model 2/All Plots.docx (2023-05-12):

Model : Force=[a_o +a_1 ε/(ε_(max))+a_2 D]P+a_3 D+a_4 ε/(ε_(max))+a_5

Regression Model: Force=B_0 +B_1 D+B_2 P+B_3 ε/(ε_(max))+B_4 DP+B_5 ε/(ε_(max))P

Optimized Parameters: ans = -201.65 8.0722 0.34124 -882.46 0.069306 0.16617


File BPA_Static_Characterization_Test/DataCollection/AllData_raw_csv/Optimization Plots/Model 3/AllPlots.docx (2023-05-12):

Model 3: Force=B_o +B_1 P+B_2 D+B_3 L+B_4 ε+B_5 ε_(max) +B_6 S+B_7 PD+B_8 ε/(ε_(max))

Optimized Parameters, B0 – > B8: 0 -0.51183 -40.164 4.5308 -6776.4 4514.1 -464.49 0.11941 633.99

Comment: Best fit curve fits most data, except for two data sets for 10mm with highest kink.


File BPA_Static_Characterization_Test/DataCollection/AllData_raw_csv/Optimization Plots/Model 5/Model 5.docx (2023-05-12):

Model 5: Force=(a_0 +a_1 Lo+a_2 (1- (∈)/(∈_max)))P+ a3(1- (∈)/(∈_max))+ a4(Lo)+ a5

- Adding L term and (1 – relative strain)
- Initial Guess : x0 = [-3.13,-1.47,21.44,2.26,-3.21,-20]


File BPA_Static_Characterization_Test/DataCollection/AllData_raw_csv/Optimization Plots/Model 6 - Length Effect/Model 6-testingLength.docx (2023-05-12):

Description: Studying the length effects

Model equation: Force = (a0 + a1L)P + a4L +a5

Hunt’s comment: Do only one variable at a time while combining all data. Do one regression fit for the combined data and plot it against Length for example.


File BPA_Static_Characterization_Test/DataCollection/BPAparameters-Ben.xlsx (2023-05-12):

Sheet: 10mm
Cut Length (lc) | Resting Length(lo) | Max Contraction Length (lmax) | Initial Kink Length (li) |  | kmax | epsilon | relative strain
13.5 | 12 | 10 | 12 | 10mm13cm all kinks | 0.1666666667 | 0 | 0
 |  |  | 11.6 |  |  | 0.03333333333 | 0.2
 |  |  | 11.2 |  |  | 0.06666666667 | 0.4
 |  |  | 10.8 |  |  | 0.1 | 0.6
23 | 21.9 | 18.6 | 21.9 | 10mm23cm all kinks | 0.1506849315 | 0 | 0
 |  |  | 20.5 |  |  | 0.06392694064 | 0.4242424242
 |  |  | 18.9 |  |  | 0.1369863014 | 0.9090909091
27.6 | 25.7 | 22.1 | 25.7 | 10mm27cm all kinks | 0.140077821 | 0 | 0
 |  |  | 25 |  |  | 0.02723735409 | 0.1944444444
 |  |  | 24.2 |  |  | 0.05836575875 | 0.4166666667
 |  |  | 22.6 |  |  | 0.1206225681 | 0.8611111111
29.8 | 28.1 | 23.6 | 28.1 | 10mm29cm all kinks | 0.1601423488 | 0 | 0
 |  |  | 26.4 |  |  | 0.06049822064 | 0.3777777778
 |  |  | 25.3 |  |  | 0.09964412811 | 0.6222222222
 |  |  | 24 |  |  | 0.1459074733 | 0.9111111111
30 | 28.1 | 24 | 28.1 | 10mm30cm all kinks | 0.1459074733 | 0 | 0
 |  |  | 26.9 |  |  | 0.04270462633 | 0.2926829268
 |  |  | 25.9 |  |  | 0.07829181495 | 0.5365853659
 |  |  | 24.8 |  |  | 0.1174377224 | 0.8048780488
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

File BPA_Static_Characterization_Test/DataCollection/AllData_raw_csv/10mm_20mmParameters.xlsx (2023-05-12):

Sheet: 10mmTest10
Model | (a0 + a1(li-lo/lo)Force + a2(li-lo)/lo + a3
Pressurizing (inflate) |  |  |  |  |  | Slope (gradient) |  | Depressurizing (deflate) |  |  |  | slope(gradient)
Data | a0 | a1 | a2 | a3 | strain (li-lo)/lo | (a0 +a1(strain)) | (a2*strain) | a0 | a1 | a2 | a3 | (a0 +a1(strain)) | (a2*strain)
10mm13cm | 0.64121 | 548.01 | 20.664 | -59.044 | 0 | 0.64121 | 0 | 0.61464 | -1837.9 | -55.513 | -52.014 | 0.61464 | 0
 | -22.774 | -702.55 | 10.75 | -130.37 | -0.03333333333 | 0.6443333333 | -0.3583333333 | -1.7336 | -69.917 | 8.2085 | -105.97 | 0.5969666667 | -0.2736166667
 | -15.079 | -235.01 | -12.203 | -195.61 | -0.06666666667 | 0.5883333333 | 0.8135333333 | -81.598 | -1232.3 | 115.6 | -157.95 | 0.5553333333 | -7.706666667
 | -10.887 | -114.23 | 238.59 | -207.51 | -0.1 | 0.536 | -23.859 | -8.4232 | -88.526 | 82.883 | -153.41 | 0.4294 | -8.2883
10mm23cm | 0.69864 | 366.76 | -5.6567 | -58.102 | 0 | 0.69864 | 0 | 0.65929 | -224.61 | 33.716 | -48.645 | 0.65929 | 0
 | -10.766 | -167.83 | 136.16 | -260.05 | -0.06818181818 | 0.6769545455 | -9.283636364 | 133.79 | 1953.2 | 47.484 | -219.31 | 0.6172727273 | -3.237545455
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

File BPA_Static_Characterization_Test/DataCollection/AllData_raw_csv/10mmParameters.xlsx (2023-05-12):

Model | (a0 + a1(li-lo/lo)Force + a2(li-lo)/lo + a3
Pressurizing (inflate) |  |  |  |  |  | Slope (gradient) |  |  | Depressurizing (deflate) |  |  |  | slope(gradient)
Data | a0 | a1 | a2 | a3 | strain (li-lo)/lo | (a0 +a1(strain)) | (a2*strain) | Intercept | a0 | a1 | a2 | a3 | (a0 +a1(strain)) | (a2*strain) | Intercept
10mm13cm | 0.64121 | 548.01 | 20.664 | -59.044 | 0 | 0.64121 | 0 | -59.044 | 0.61464 | -1837.9 | -55.513 | -52.014 | 0.61464 | 0 | -52.014
 | -22.774 | -702.55 | 10.75 | -130.37 | -0.03333333333 | 0.6443333333 | -0.3583333333 | -130.7283333 | -1.7336 | -69.917 | 8.2085 | -105.97 | 0.5969666667 | -0.2736166667 | -106.2436167
 | -15.079 | -235.01 | -12.203 | -195.61 | -0.06666666667 | 0.5883333333 | 0.8135333333 | -194.7964667 | -81.598 | -1232.3 | 115.6 | -157.95 | 0.5553333333 | -7.706666667 | -165.6566667
 | -10.887 | -114.23 | 238.59 | -207.51 | -0.1 | 0.536 | -23.859 | -231.369 | -8.4232 | -88.526 | 82.883 | -153.41 | 0.4294 | -8.2883 | -161.6983
10mm23cm | 0.69864 | 366.76 | -5.6567 | -58.102 | 0 | 0.69864 | 0 | -58.102 | 0.65929 | -224.61 | 33.716 | -48.645 | 0.65929 | 0 | -48.645
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

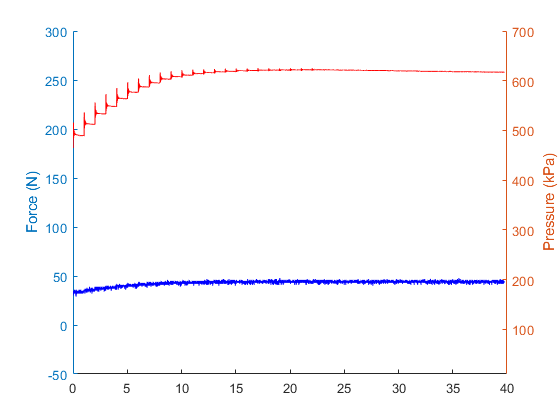
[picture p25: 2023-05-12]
BPA_Static_Characterization_Test/PWM_valve_noleak_arduinooutputloadcell.png

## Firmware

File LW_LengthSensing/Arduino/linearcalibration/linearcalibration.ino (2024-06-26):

//Attempt to make te linear calibration process more automatic

// Assigning Linear Potentiometer to Analog Input A0, pressure sensor to A2, and solenoid valve to 7
  const int pot = A0;
  const int psensor = A2; 
  const int straingauge = A5;
  //float strainval[2];
  //float strainfiltval;
 // int solenoidPin = 10;
  #define PWM_PIN 6
  #define solenoidPin 10
  int pwmValue = 0 ;
  int pinState = LOW;
  unsigned long previousMillis = 0;
  const long interval = 1000;
  const long rampDuration = 4000;

//Pulse Information

  int delayBetweenPulses = 1000; // Initial delay between pulses in milliseconds, starting at 500ms
  const int pulseWidth = 35;    // Width of each pulse in milliseconds
  bool isPumpingFirst = false;  // Flag indicating whether the pump is currently active for the first pulse
  bool isPumpingSecond = false; // Flag indicating whether the pump is currently active for the second pulse
  unsigned long delayZeroTime = 0; // Timestamp when delay between pulses first reaches zero
  bool continueRunning = true; // Flag to control the execution of the main loop


void setup() {

  //Set PWM resolution to 12 bits (0-4095)
  analogWriteResolution(12);
  pinMode(PWM_PIN,OUTPUT);

  //Establish the solenoid pin as an OUTPUT
  pinMode(solenoidPin, OUTPUT);

  // Start serial communication
  Serial.begin(9600);
}

void loop() {

  unsigned long currentMillis = millis();
  // Check if data is available to read from serial port
  if (Serial.available() > 0) {
    // Read the incoming character
    char command = Serial.read();

    // Check if the command is 'R'
    if (command == 'R') {
     // if (currentMillis - previousMillis >= interval) {
       // previousMillis = currentMillis;
       if (pwmValue == 0);

        writeData();
        pwmValue = 1500; //Hop from 0 to 1500
        analogWrite(PWM_PIN, pwmValue);
        
    } else {
        // Increment the PWM value by 500 (adjust as needed)

        writeData();
        pwmValue += 500; 

        // Ensure the PWM value stays within the acceptable range (0-4096)
        pwmValue = constrain(pwmValue, 0, 4096);

        analogWrite(PWM_PIN, pwmValue);

    }
  }

  // Add any other code needed for your application
  // For example, additional sensors reading or control logic
}

void writeData() {
      float potValue = analogRead(pot);
      float pValue = analogRead(psensor);
      float strainvoltage = analogRead(straingauge);

      float straindisp = strainvoltage * 0.066573 + 41.652;

      float displacement = potValue*0.1013782991; //new calibration
      float pressure = pValue*0.1084 - 2.1067;

      
      // Send the measurement back to MATLAB
      Serial.println(displacement);
      Serial.println(strainvoltage);

}

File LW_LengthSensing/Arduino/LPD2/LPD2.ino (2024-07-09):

//Real-time Length Sensing
//By: Rochelle Jubert
//MOLLY USE THIS ONE

//Use Linear Potentiometer to measure real-time displacement of pneumatic-actuated artifical muscle

//notes:
// -Tell the valve to stop opening and closing after a certian number of cycles. Use counter?
// -Write two separate codes for short term and long-term
// -Make sure the writing to the SDcard lines up with valve actuating
// -Address the delay 
// -There's a delay actuating the valve when the SDcard is writing 
// -Does the delay in the blink code delay the whole code?


// Assigning Linear Potentiometer to Analog Input A0, pressure sensor to A2, and solenoid valve to 7
  const int pot = A0;
  const int psensor = A2; 
  const int straingauge = A5;
  //float strainval[2];
  //float strainfiltval;
 // int solenoidPin = 10;
  #define PWM_PIN 6
  #define solenoidPin 10
  int pwmValue = 0 ;
  int pinState = LOW;
  unsigned long previousMillis = 0;
  const long interval = 1000;
  const long rampDuration = 4000;

//Pulse Information

  int delayBetweenPulses = 1000; // Initial delay between pulses in milliseconds, starting at 500ms
  const int pulseWidth = 35;    // Width of each pulse in milliseconds
  bool isPumpingFirst = false;  // Flag indicating whether the pump is currently active for the first pulse
  bool isPumpingSecond = false; // Flag indicating whether the pump is currently active for the second pulse
  unsigned long delayZeroTime = 0; // Timestamp when delay between pulses first reaches zero
  bool continueRunning = true; // Flag to control the execution of the main loop


void setup() {

//Set PWM resolution to 12 bits (0-4095)
  analogWriteResolution(12);
  pinMode(PWM_PIN,OUTPUT);

// Establishing serial communication between Arduino and computer
  Serial.begin(9600);

//Establish the solenoid pin as an OUTPUT
  pinMode(solenoidPin, OUTPUT);
}
void loop() {

  //OPTION 1: Actuate the solenoid valve using the transistor (Binary ON/OFF Solenoid)
    // unsigned long currentMillis = millis();
    //   writeData();    

    //   if (currentMillis - previousMillis >= interval) {
    //     // save the last time you blinked the LED
    //       previousMillis = currentMillis;

    //     // if the LED is off turn it on and vice-versa:
    //       if (pinState == LOW) {
    //         pinState = HIGH;
    //       } else {
    //         pinState = LOW;
    //   }

    //   // set the LED with the ledState of the variable:
    //   digitalWrite(solenoidPin, pinState);
    // }

    //analogWrite(PWM_PIN, pwmValue);

  //OPTION 2: This is creating steps using the proportional solenoid valve
    // if (currentMillis - previousMillis >= interval) {
    //   previousMillis = currentMillis;
    
    //   // Increment the PWM value by 1024 (adjust as needed)
    //   pwmValue += 1024; //1024;

    //   // Ensure the PWM value stays within the acceptable range (0-4096)
    //   pwmValue = constrain(pwmValue, 0, 4096);

    //   analogWrite(PWM_PIN, pwmValue);
    // }
    

  //OPTION 3: Ramp code    
    // rampUp();
    // delay(20);  // Delay for 1 second between ramps
    // rampDown();
    // delay(20);

  //Option 4: Hold Up and Hold Down
    // holdup();
    // delay(1);
    // holddown();
    // delay(1);

  //Option 5: Ramp and Hold
    // rampUp();
    // delay(1);
    // holdup();
    // delay(1);
    // rampDown();
    // delay(1);
    // holddown();

  //OPTION 6: 2 valve configuration
    // unsigned long currentMillis = millis();
    // //writeData();

    //   if (currentMillis - previousMillis >= interval) {
    //     // save the last time you blinked the LED
    //       previousMillis = currentMillis;

    //     // if the LED is off turn it on and vice-versa:
    //       if (pinState == LOW) {
    //         pinState = HIGH;
    //         pwmValue = 0;
    //         // set the LED with the ledState of the variable:
    //           digitalWrite(solenoidPin, pinState);
    //           analogWrite(PWM_PIN, pwmValue);
    //       } else {
    //         pinState = LOW;
    //         pwmValue = 100;
    //         // set the LED with the ledState of the variable:
    //           digitalWrite(solenoidPin, pinState);
    //           analogWrite(PWM_PIN, pwmValue);
    


     //}

  //Option 7: Pulsing
    // unsigned long currentMillis = millis();
    // unsigned long timeSinceLastIntervalStart = currentMillis - previousMillis; // Time since the last interval start
    // writeData();

    // if (!continueRunning) {
    // return; // Exit the loop if the continueRunning flag is false
    // }

    // // Pulse control logic for the first pulse
    //   if (timeSinceLastIntervalStart < pulseWidth && !isPumpingFirst) {
    //     digitalWrite(solenoidPin, HIGH); // Activate the pump for the first pulse
    //     isPumpingFirst = true;
    //   } else if (timeSinceLastIntervalStart >= pulseWidth && isPumpingFirst) {
    //     digitalWrite(solenoidPin, LOW); // Deactivate the pump after the first pulse
    //     isPumpingFirst = false;
    //   }

    // // Pulse control logic for the second pulse
    //   if (timeSinceLastIntervalStart >= delayBetweenPulses && timeSinceLastIntervalStart < delayBetweenPulses + pulseWidth && !isPumpingSecond) {
    //     digitalWrite(solenoidPin, HIGH); // Activate the pump for the second pulse
    //     isPumpingSecond = true;
    //   } else if (timeSinceLastIntervalStart >= delayBetweenPulses + pulseWidth && isPumpingSecond) {
    //     digitalWrite(solenoidPin, LOW); // Deactivate the pump after the second pulse
    //     isPumpingSecond = false;
    //   }

    // // Adjust delay between pulses at the end of the interval
    //   if (timeSinceLastIntervalStart >= interval) {
    //     previousMillis = currentMillis; // Reset the interval timer for the next cycle

    // // Adjust delay between pulses at the end of the interval
    //   if (timeSinceLastIntervalStart >= interval) {
    //   previousMillis = currentMillis; // Reset the interval timer for the next cycle

    //   // Adjust delay between pulses according to the specified logic
    //     if (delayBetweenPulses >= 1000) {  //for range of > 1000 , reduce by 100ms per interval
    //       delayBetweenPulses -= 100;
    //     } else if (delayBetweenPulses >= 500) { //for range of 1000 to 500ms, reduce by 50ms per interval
    //       delayBetweenPulses -= 50;
    //     } else if (delayBetweenPulses >= 250) { //for range of 500 to 250ms, reduce by 25ms per interval
    //       delayBetweenPulses -= 25;
    //     } else if (delayBetweenPulses >= 100) { //for range of 250 to 100ms, reduce by 15ms per interval
    //       delayBetweenPulses -= 15;
    //     } else if (delayBetweenPulses > 0) {    //for range of 100 to 0ms, reduce by 10ms per interval
    //       delayBetweenPulses -= 10;
    //     }

    //   // Ensure delayBetweenPulses doesn't go below 0
    //     if (delayBetweenPulses < 0) {
    //       delayBetweenPulses = 0;
    //     }

    //   // Record the time when delay between pulses first reaches zero
    //     if (delayBetweenPulses <= 25 && delayZeroTime == 0) {
    //       delayZeroTime = currentMillis;
    //     }

    //   // Check if we should stop running after a certain time with zero delay
    //     if (delayZeroTime > 0 && (currentMillis - delayZeroTime >= 0)) {
    //       continueRunning = false; // Stops the loop after 4 seconds of zero delay
    //     }
    //   }
    
    //   }

  //Option 8: Random PWM Signal
    // unsigned long startTime = millis();
    // unsigned long currentTime;
    // int currentValue = 0;
    // int targetValue = 0;

    // while ((currentTime = millis()) - startTime < 40000) {
    //   // Generate a random target value
    //   targetValue = random(4095 + 1);
    
    //   // Ramp up or down to the target value
    //     while (currentValue != targetValue) {
    //       if (currentValue < targetValue) {
    //         currentValue +=120;
    //         if (currentValue > targetValue) {
    //           currentValue = targetValue;
    //         }
    //       } else {
    //         currentValue-=120;
    //         if (currentValue < targetValue){
    //           currentValue = targetValue;
    //         }
    //       }
    //       analogWrite(PWM_PIN, currentValue);
    //       writeData();
    //       delay(1); // adjust the speed of the ramp
    //     }
    
    //   // Wait for a random amount of time before changing the target value
    //     delay(random(10, 100)); // adjust the range of delay
    // }

  //Option 9: Ramp Air + Quick Release
  //Have proportional valve in line with solenoid to release
    // delay(1);
    // rampUp();
    // delay(1);
    // open();

  //Option 10: Quick Fill + Ramp Release
  //Have solenoid in line with proportional valve to release, change rampUp mapping to 200, 4095 (adjust as needed)
    open2();
    delay(1);    
    rampUp();
    delay(1);

}

void open() {
  unsigned long startTime = millis();
  unsigned long currentTime;
  int pwmValue;

  while ((currentTime = millis()) - startTime <= interval) {
    pwmValue = 0;
    digitalWrite(solenoidPin, HIGH); 
    writeData(pwmValue);
    delay(10);  // Adjust delay as needed for smoother ramp
    
  }
    digitalWrite(solenoidPin, LOW);  // Ensure PWM is off at the end
}

void open2() {
  unsigned long startTime = millis();
  unsigned long currentTime;
  int pwmValue;

  while ((currentTime = millis()) - startTime <= interval) {
    digitalWrite(PWM_PIN, 0);
    digitalWrite(solenoidPin, HIGH); 
    writeData(pwmValue);
    delay(10);  // Adjust delay as needed for smoother ramp
    
  }
   digitalWrite(solenoidPin, LOW);  // Ensure PWM is off at the end
}

void rampUp() {
  unsigned long startTime = millis();
  unsigned long currentTime;
  int pwmValue;

  while ((currentTime = millis()) - startTime <= rampDuration) {
    pwmValue = map(currentTime - startTime, 0, rampDuration, 200, 4095);
    analogWrite(PWM_PIN, pwmValue);
    writeData(pwmValue);
    delay(10);  // Adjust delay as needed for smoother ramp
  }

  analogWrite(PWM_PIN, 0);  // Ensure PWM is off at the end
}

void rampDown() {
  unsigned long startTime = millis();
  unsigned long currentTime;
  int pwmValue;

  while ((currentTime = millis()) - startTime <= rampDuration) {
    pwmValue = map(currentTime - startTime, 0, rampDuration, 4095, 0);
    analogWrite(PWM_PIN, pwmValue);
    writeData(pwmValue);
    delay(10);  // Adjust delay as needed for smoother ramp
  }

  analogWrite(PWM_PIN, 0);  // Ensure PWM is off at the end
}

void holdup() {
  unsigned long startTime = millis();
  unsigned long currentTime;
  int pwmValue;

  while ((currentTime = millis()) - startTime <= interval) {
    pwmValue = 4095;
    analogWrite(PWM_PIN, pwmValue);
    writeData(pwmValue);
    delay(10);  // Adjust delay as needed for smoother ramp
  }

  analogWrite(PWM_PIN, 0);  // Ensure PWM is off at the end
}

void holddown() {
  unsigned long startTime = millis();
  unsigned long currentTime;
  int pwmValue;

  while ((currentTime = millis()) - startTime <= interval) {
    pwmValue = 0;
    analogWrite(PWM_PIN, pwmValue);
    writeData(pwmValue);
    delay(10);  // Adjust delay as needed for smoother ramp
  }

  analogWrite(PWM_PIN, 0);  // Ensure PWM is off at the end
}
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

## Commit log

2021-01-19 initial commit for muscle sensory
    [sensorCap.SLDPRT, sensorCap.STL, sensorEnd.SLDASM, sensorEnd.SLDPRT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]
2021-01-19 rename directory
    [sensorCap.SLDPRT, sensorCap.STL, sensorEnd.SLDASM, sensorEnd.SLDPRT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]
2021-01-19 Added two folders
    Added folder BPA end caps. This is taken from the AARL puppy model. Parts 18_02_01_010 and _011 are the port and cap, respectively, for the Festo 10 mm BPAs. Similarly, parts _012 and _013 are for th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
    Added folder Living Machines 2021 - BPA Test for the components that are going to be used in the BPA characterization static test being headed by Lawrence.
    [8020-1515 X 15.SLDPRT, 8020-1515 X 36.SLDPRT, AARL_Puppy_18_02_01_000.SLDASM, AARL_Puppy_18_02_01_001.SLDPRT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]
2021-01-19 continued design for TOF IR sensor housing
    [sensorCap.SLDPRT, sensorEnd.SLDPRT]
2021-01-19 tuning some dimensions
    [sensorEnd.SLDPRT]
2021-01-19 create cable route
    [sensorCap.SLDPRT]
2021-01-19 update assembly
    [sensorEnd.SLDASM]
2021-01-19 reorganzing some files
    [sensorCap.SLDPRT, sensorCap.STL, sensorEnd.SLDASM, sensorEnd.SLDPRT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]
2021-01-20 calculate the size of o ring
    [O_Ring_calculator.xlsx]
2021-01-20 change fill hole size
    [sensorCap.SLDPRT]
2021-01-20 update STL
    [sensorCap.STL, sensorEnd.STL]
2021-01-21 tune dimensioning
    [sensorCap.SLDPRT, sensorEnd.SLDASM, sensorEnd.SLDPRT]
2021-01-25 housing for Ultrasonic sensor for testing
    [sensorHousing.SLDPRT, sensorHousing.STL]
2021-01-25 update correct diameter
    [sensorHousing.SLDPRT, sensorHousing.STL]
2021-01-27 redesign for snap fit
    [sensorCap_snapfit.SLDPRT, sensorEnd_snapfit.SLDPRT]
2021-01-27 redesign for printability
    [sensorCap_snapfit.SLDPRT, sensorCap_snapfit.STL]
2021-01-27 create circular housing design
    [sensorCap_circularHousing.SLDPRT, sensorEnd_CircularHousing.SLDPRT]
2021-01-27 update latching mechanism
    [sensorCap_circularHousing.SLDPRT]
2021-01-27 update dimensions
    [sensorCap_circularHousing.STL, sensorEnd_circularHousing.STL]
2021-01-28 update assembly for circular housing design
    [capEnd_circularHousing.SLDASM]
2021-01-30 test stand for 45 degree and perpendicular setup
    [testStand.SLDPRT]
2021-01-31 redesign to hold the sensor
    [testStand.SLDPRT]
2021-01-31 fine tune some dimensions for better fit
    [testStand.SLDPRT, testStand.STL]
2021-01-31 adjust for better surface contact for boucing the beam
    [testStand.SLDPRT, testStand.STL]
2021-01-31 update teststand to help with scattering
    [testStand.SLDPRT, testStand.STL]
2021-02-01 update with built-in support
    [sensorCap_circularHousing.SLDPRT, sensorEnd_CircularHousing.SLDPRT]
2021-02-01 add some fillets
    [sensorCap_circularHousing.SLDPRT]
2021-02-01 test stand for direct configuration.
    [testStand_direct.SLDPRT]
2021-02-01 test stand for the 45 degree config
    [testStand_45deg.SLDPRT]
2021-02-01 small modifications
    [testStand_direct.SLDPRT]
2021-02-02 Assembly modification
    Put 8.5" crossmembers in. Deleted 15" crossmembers.
    [1515_8_5_CL.sldprt, 8020-1515 X 15.SLDPRT, Static Test Assembly - 10mm.SLDASM]
2021-02-03 update STL for printing
    [sensorCap_circularHousing.STL, sensorEnd_circularHousing.STL]
2021-02-03 adjust tolerance
    [sensorCap_circularHousing.SLDPRT]
2021-02-03 adjust color
    [sensorCap_circularHousing.SLDPRT, sensorEnd_CircularHousing.SLDPRT]
2021-02-03 add model of the IR sensor
    [vl53l0x-vl53l1x-vl53l3cx-carrier-model (1).step, vl53l0x-vl53l1x-vl53l3cx-carrier-model (1).step.SLDPRT]
2021-02-03 Create 1173N023_ULTRA-COMPRESSIBLE O-RING.SLDPRT
    [1173N023_ULTRA-COMPRESSIBLE O-RING.SLDPRT]
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2021-02-05 tune some tolerances
    [sensorCap_circularHousing.SLDPRT, sensorCap_circularHousing.STL]
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2021-02-06 update tolerances
    [sensorCap_circularHousing.SLDPRT, sensorCap_circularHousing.STL, sensorEnd_CircularHousing.SLDPRT]
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2021-02-06 readjust for better fit and tightness
    [sensorCap_circularHousing.SLDPRT, sensorCap_circularHousing.STL, sensorEnd_CircularHousing.SLDPRT, sensorEnd_circularHousing.STL]
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2021-02-08 adjust tolerance for easier fit
    [sensorCap_circularHousing.SLDPRT, sensorCap_circularHousing.STL]
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2021-03-05 Revert "10mm assembly finished"
    This reverts commit 974d73d23ba0833a320319935f1551bd0383e953.
    [AARL_Puppy_18_02_01_009-5388K140_Hose-Clamp.SLDPRT, BPAtoMeter.SLDPRT, MeterToFrame.SLDPRT, Static Test Assembly - 10mm.SLDASM]
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2021-03-09 Revert "Renamed folders. Modified part."
    This reverts commit 672bef0e728703cbe3eb6821429b1f958307d69c.
    [1515_8_5_CL.sldprt, 8020-1515 X 36.SLDPRT, AARL_Puppy_18_02_01_009-5388K140_Hose-Clamp.SLDPRT, BPAConnectionToFrame4.SLDPRT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]
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2021-03-09 doesn't make sense
    ugggghh
    [AARL_Puppy_18_02_01_009-5388K140_Hose-Clamp.SLDPRT, BPAtoMeter.SLDPRT, MeterToFrame.SLDPRT, Static Test Assembly - 10mm.SLDASM]
2021-03-09 Revert "Revert "10mm assembly finished""
    This reverts commit 1d11ba11227d5d9cf286d5f312e0a6b532e36a7c.
    [AARL_Puppy_18_02_01_009-5388K140_Hose-Clamp.SLDPRT, BPAtoMeter.SLDPRT, MeterToFrame.SLDPRT, Static Test Assembly - 10mm.SLDASM]
2021-03-09 Fixed folders and parts
    This is a real revert to the final products. Deleted Living Machines folder. All parts in BPA static characterization folder.
    [1515_8_5_CL.sldprt, 8020-1515 X 36.SLDPRT, BPAConnectionToFrame4.SLDPRT, BPAtoMeter.SLDPRT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]
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2021-03-14 redesign to flip the probe side
    [testStandProbe_dualSensor_BPA.SLDPRT, testStandProbe_dualSensor_BPA.STL]
2021-03-14 initial commit for mounting to the 80 20 test fixture
    [80_20_BPA_mounting.SLDPRT, 80_20_BPA_mounting.STL]
2021-03-14 modify fill ports design for the test fixture
    [modified_AARL_Puppy_18_02_01_012_Festo20mm_U10port.SLDPRT, modified_AARL_Puppy_18_02_01_012_Festo20mm_port.SLDPRT]
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2021-03-14 rename for consistency, fix mate error
    [capEnd_circularHousing.SLDASM, circularHousing.SLDASM]
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2021-03-14 add assembly file for the test fixture
    [testFixtureAssembly.SLDASM]
2021-03-14 update new port for test fixture assembly
    [testFixtureAssembly.SLDASM]
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2021-03-14 add STL and minor fixes
    [80_20_sensorMounting.SLDPRT, 80_20_sensorMounting.STL]
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2021-04-21 20mm configuration
    Added PlugForFrame_20 and BPAConnectionToFrame_20 to Static Test Assembly 20mm configuration. This configuration still needs a BPAtoMeter_20 that hasn't been design yet. It also needs appropriate siz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
    [BPAConnectionToFrame4.SLDPRT, BPAConnectionToFrame_10.SLDPRT, BPAConnectionToFrame_20.SLDPRT, BPAtoMeter.SLDPRT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]
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2021-08-04 Edited tolerance on meter-hook assembly 10
    [BPA10-Hook Assembly.SLDASM, BPA10toMeter_003.SLDPRT, Hook_002.SLDPRT, MeterToFrame_002.SLDPRT]
2021-08-04 re-dimensioning for tolerance
    [BPA10-Hook Assembly.SLDASM, BPA10toMeter_003.SLDPRT, BPA20toMeter_004.SLDPRT, Hook_002.SLDPRT]
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2022-03-11 correcting 10mm and 20mm data
    [10mm_13cm_Kinked12mm_Test1.csv, 10mm_13cm_Kinked12mm_Test10.csv, 10mm_13cm_Kinked12mm_Test2.csv, 10mm_13cm_Kinked12mm_Test3.csv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]
2022-03-12 Correcting 20mm Data
    [Data Collection Notes.xlsx]
2022-03-12 Corrected 20mm Data
    [20mm_10cm_Kinked13mm_Test10Data.csv, 20mm_10cm_Kinked13mm_Test1Data.csv, 20mm_10cm_Kinked13mm_Test2Data.csv, 20mm_10cm_Kinked13mm_Test3Data.csv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]
2022-03-15 Corrected 10mm data
    [10mm_13cm_Kinked12mm_Test1.csv, 10mm_13cm_Kinked12mm_Test10.csv, 10mm_13cm_Kinked12mm_Test2.csv, 10mm_13cm_Kinked12mm_Test3.csv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]
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2022-05-04 Optimizing and fixing 20mm data
    [BPArecordings.xlsx]
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2022-08-15 Optimization
    -new equation to include kmax
    - note: issues with plotting when using new equation
    [10mmParameters.xlsx, 20mmParameters.xlsx, AllBPA10mm13cm_DP_test9parameters.csv, AllBPA10mm13cm_P_test9parameters.csv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]
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2022-08-26 Revert "regression code for optimization"
    This reverts commit 1e56db4f3ad40cabc5a7ecd2046e77c585609675.
    [BPAparameters-Ben.xlsx, BPAparameters_normalized.xlsx, BPArestingLength_maxStrain.xlsx, Optimization_Parameters.xlsx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]
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2022-09-14 Revert "Merge branch 'PWMTesting_2_Lawrence' of https://github.com/Agile-and-Adaptive-Robotics/Muscle_Sensory into PWMTesting_2_Lawrence"
    This reverts commit af80296e510cfab2e62d151d5f14bbf5597082b6, reversing
    changes made to ba956a58db6c06af00cd21b725bdbe5ae0ac15a8.
    [10mmParameters.xlsx, 10mm_20mmParameters.xlsx, 2022Jan27_LoadCalibration.xlsx, 20mmParameters.xlsx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]
2022-09-14 Revert "?"
    This reverts commit ba956a58db6c06af00cd21b725bdbe5ae0ac15a8.
    [BPAparameters.xlsx]
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2022-09-21 Revert "Merge branch 'PWMTesting_2_Lawrence' of https://github.com/Agile-and-Adaptive-Robotics/Muscle_Sensory into PWMTesting_2_Lawrence"
    This reverts commit 3635a65fdf8473165e8b58d0190dd0391cfc9739.
    [10mmParameters.xlsx, 10mm_20mmParameters.xlsx, 2022Jan27_LoadCalibration.xlsx, 20mmParameters.xlsx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]
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2022-09-29 Model 8 - plotting optimized parameters
    Model doesn't fit all data
    [OptimizingParameters.xlsx]
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2022-11-30 20mm
    too many issues collecting data.
    [BPAparameters.xlsx, BPAparameters_.xlsx]
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
